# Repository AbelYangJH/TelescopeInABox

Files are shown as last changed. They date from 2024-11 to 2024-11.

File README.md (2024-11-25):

# TelescopeInABox
The Telescope In A Box is a collapsible Dobsonian Telescope

There are two models available:

- Model 2: Designed for a 114mm dia f/8 primary mirror
- Model 3: Designed for a 200mm dia f/5 primary mirror

A more detailed paper is available at https://www.worldscientific.com/doi/abs/10.1142/S2661339521500049

To cite:
> The Telescope-in-a-Box — A Collapsible Open-Frame Dobsonian Telescope for Student Astronomy Projects
> 
> A. Yang, A. H. Chan, and S. C. Cindy Ng
> 
> The Physics Educator Vol. 03, No. 01, 2150004 (2021)

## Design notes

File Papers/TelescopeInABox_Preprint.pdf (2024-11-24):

The Physics Educator
c World Scientific Publishing Company

## The Telescope-in-a-box - A collapsible open-frame Dobsonian Telescope for Student Astronomy Projects

A. Yang∗

, A. H. Chan†

, S. C. Cindy Ng.‡
Department of Physics, National University of Singapore, 2 Science Drive 3, Block S12, Level 2, Singapore 117551 ∗phyyja@nus.edu.sg
†phycahp@nus.edu.sg
‡phynsc@nus.edu.sg

Received Day Month Year
Revised Day Month Year

The telescope-in-a-box is a small objective ultralight Dobsonian telescope concept that will be accompanied by telescope instrumentation lesson plans. This provides a rich set of opportunities for teaching astronomy, physics and engineering. Our first two prototypes demonstrate that it can be constructed at low cost, while many of the design decisions can lead to lesson plans in telescope instrumentation.

Keywords: Telescopes; Practical Astronomy; Astronomical Instrumentation.

### 1. Introduction

Telescopes are an essential teaching tool in astronomy¹
, allowing students to connect in-class instruction to the real world through practical activities²
. However, many commercial telescopes are large and bulky, or have limited light collecting area. In particular, many commercially available small telescopes are of the closed tube design, while truss or ultralight designs are commercially available only for larger aperture reflectors (generally 300mm objective diameter and larger) and tend to be more expensive.
These limitations place some constraints on the use of commercially available small telescopes in a classroom setting. The closed tube design of the more affordable models limit the in-class demonstration potential in that students do not necessarily get to see the inner workings of the telescope and tend to treat it as some sort of black box. At the same time, the higher cost of the truss or ultralight models mean that mass deployment of such models are far less feasible. To solve this problem, we have developed the telescope-in-a-box, a small objective ultralight Dobsonian telescope that is inexpensive, collapsible and lightweight with an open frame. This concept is based on the guiding principles of portability, cost and educational value.
To be portable, the telescope needs to be both lightweight and collapsible. The first prototype of the telescope-in-a-box proved that a collapsible design is practical, but its carrying weight will strongly depend on the choice of materials and engineering decisions that go into the final design. In contrast with commercial ultralight Dobsonians which are designed to be lightweight first, the telescope-in-a-box is designed to be compact first, with the intention that students may borrow a telescope set for independent observations. This is especially important because in Singapore, students generally travel by public transport and that makes a large bulky tube less practical to transport. In many other parts of Southeast Asia, students often

1

2 A. Yang et. al.

travel via motorcycle which also does not allow for transporting of a large bulky tube.
To be low-cost, we need to carefully choose the objective size and structural materials. In contrast with commercial ultralight or truss Dobsonians, the telescope-in-a-box has a much smaller objective diameter. This is particularly important since the cost of a Dobsonian is primarily driven by its objective diameter.
More importantly, the telescope-in-a-box must have a rich set of educational opportunities in the classroom and in the field. That means the telescope design must be sufficiently capable on its own, while at the same time provide sufficient educational opportunities through its design. A good example of how this is accomplished is the gallileoscope³
, which
is a simple refractor that is designed to be taken apart and assembled in class, with ample opportunities to demonstrate optical principles⁴
. While the
gallileoscope was originally developed for the price point of 30 USD and does not include a tripod, the telescope-in-a-box that we have built costs about 250 USD which includes a simple Dobsonian mount.

### 2. The Tubeless Telescope-in-a-box

prototypes

In the course of its design and construction, we have constructed two prototypes for the telescope-in-abox. Prototype 1 has a 200mm f/6 primary mirror, with a focal length of 1200mm and was constructed to demonstrate the tubeless design with off-the-shelf mirror cells and focuser. In addition, the carrying case was also designed to double up as the azimuth base and rocker box. However, that meant the carrying case needed to be stronger and hence heavier. In addition, the primary mirror cell was an off-the-shelf part that was excessively heavy, but extremely sturdy. The secondary support pole used a 30mm aluminium T-slot extrusion, which is readily available and sturdy, but also very heavy. The final carrying weight of prototype 1 is 21 kg. Prototype 2 was constructed as an attempt to improve on the basic Newtonian design in addition to the tubeless design. It has a 112.5 mm f/8 primary mirror with a focal length of 900mm (taken from an existing Newtonian telescope) and was constructed to be lightweight and compact. In its collapsed form, the main parts can be packed in a small plastic box (excluding the poles and base). In particular, prototype 2 uses custom 3D printed parts (printed on a modified Flashforge Creator Pro) including the mirror cells and focuser and has a much larger altitude bearing.
In addition, prototype 2 was designed to be assembled without any special tools; It only requires a simple screwdriver for secondary collimation. To make the final design lightweight, we chose not to use the carrying case as a structural component, while the secondary support is a pair of lightweight wooden (paulownia) poles. The final carrying weight of prototype 2 is less than 3kg.

### 2.1. Design Decisions

In the course of the design and construction process, we note that the use of custom-designed parts allow for a closer examination of the physical principles underlying telescope design, and potentially allows for the teaching of iterative design methods. For example, the focuser in prototype 2 is a threaded rotating helical focuser which took multiple tries to perfect, because of manufacturing tolerance issues. To solve this, the final design used a compliant split thread that would hold the focuser tube, while at the same time be tolerant of less than ideal manufacturing precision. Similar concepts can be taught, and the choice of focuser design can also be a potential lesson plan.
In addition, the design of the mirror cells provides an opportunity to discuss the concept of kinematic couplings and degrees of freedom, while the design decisions that go into the secondary pole provide an opportunity to examine beam deflection, centre of mass and material selection. This is in contrast to the use of off-the-shelf parts such as mirror cells and focusers which lock the user in to a triedand-tested design paradigm.
The use of custom parts for prototype 2 did not result in any significant additional costs beyond 3D printing, with the final bill of materials for prototype 2 being less than USD 200. Here, the single most expensive part is the mirror set (a new mirror set with similar specifications costs USD 90; http://www.e-scopes.cc/), although it is certainly possible for amateurs to grind their own primary mirror. Amateur telescope makers have made telescopes with little more than plywood, cardboard and carpentry skills.
For prototype 2 much time was spent on multiple design iterations. While this may seem to be a disadvantage, the design iterations provide a handson experience on how the parts fit together, and the physical principles that go into the design, from

The Telescope-in-a-box 3

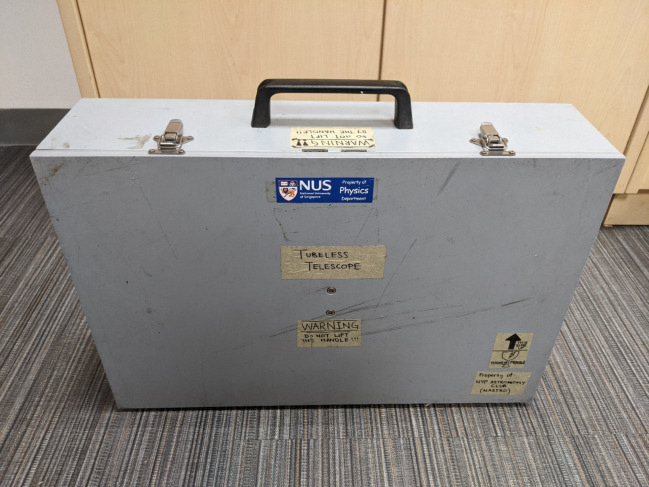
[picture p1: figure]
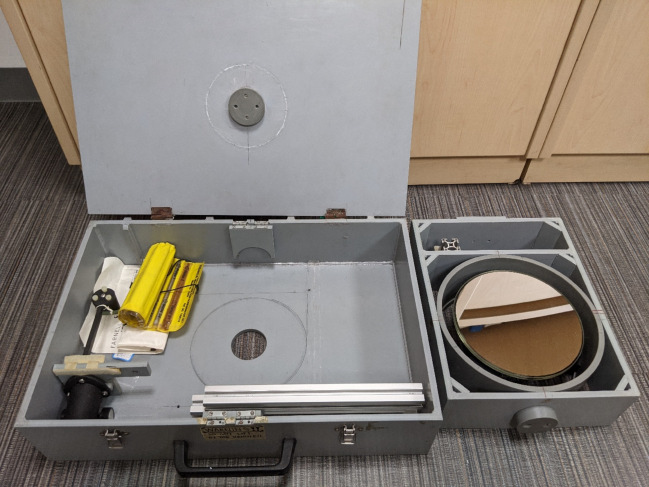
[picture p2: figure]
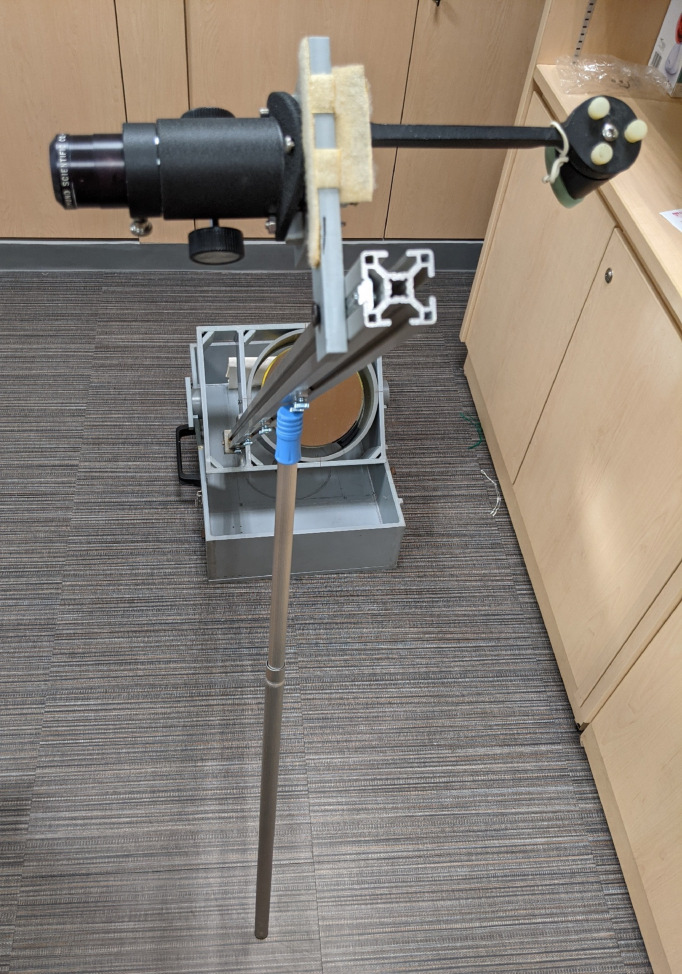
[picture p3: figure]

i.

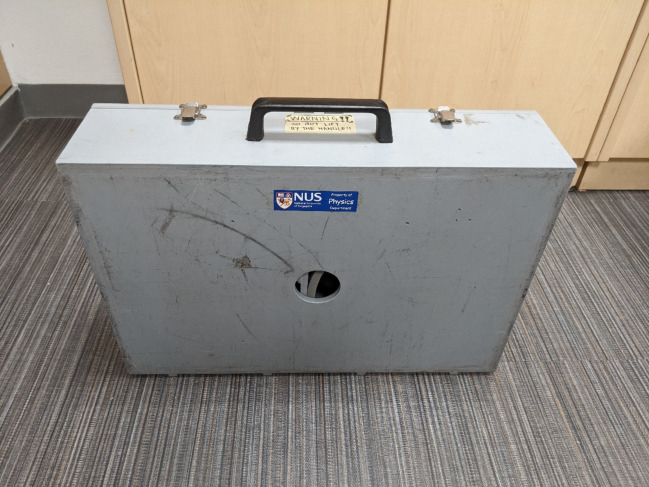
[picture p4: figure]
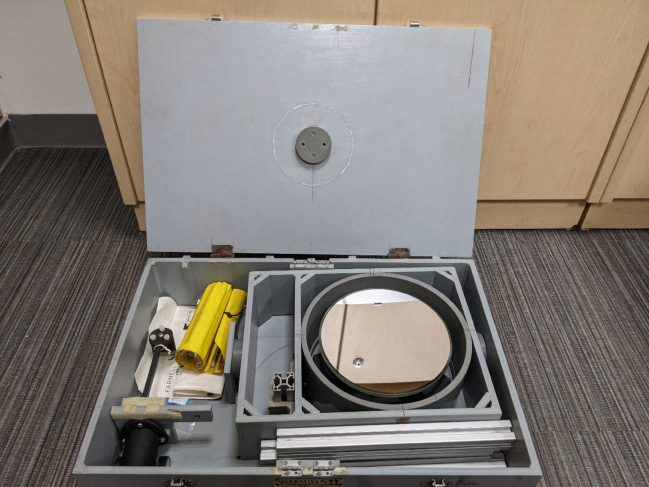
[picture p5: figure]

a. | b. | c.

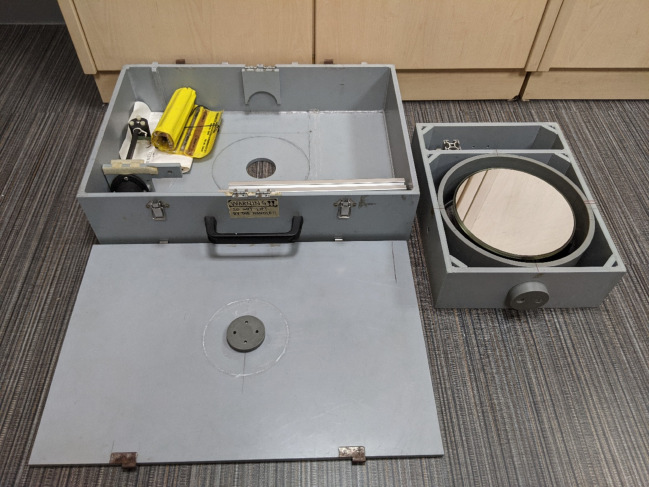
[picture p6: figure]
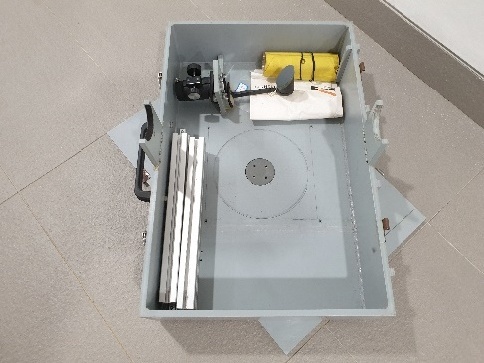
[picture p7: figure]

d. | e. | f.

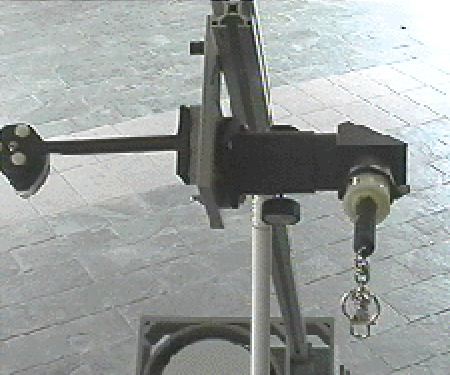
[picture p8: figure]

g.

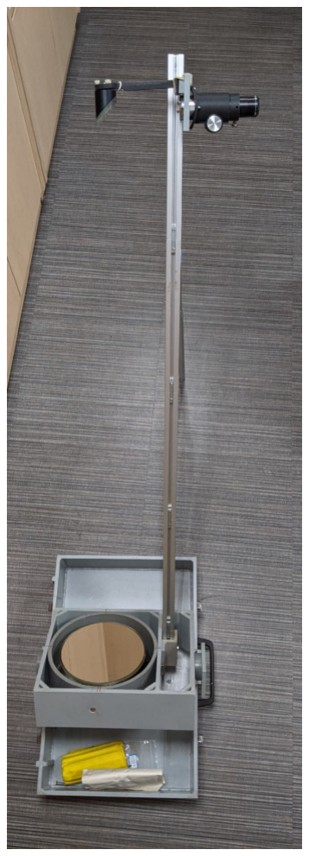
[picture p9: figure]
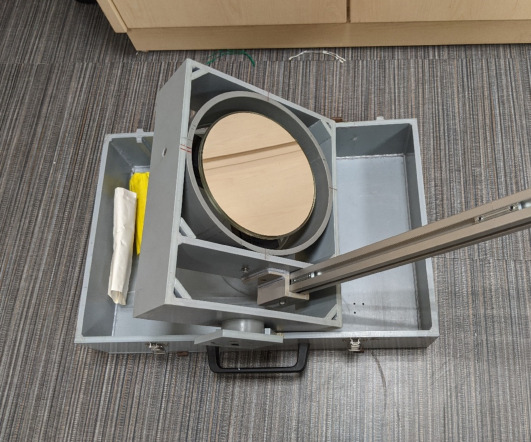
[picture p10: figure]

h. j.

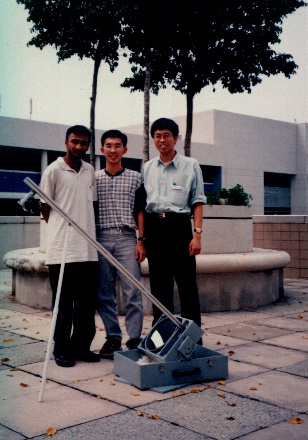
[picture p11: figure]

k.

Fig. 1. Tubeless Telescope in a box prototype 1. | a. Front view. | b. Back view (note the round hole). | c. Contents of the
box with accessories. | d. The primary mirror box taken out. | e. The separated cover (note the round peg). | f. The box is
placed on the cover and can be rotated about the peg. | g. The secondary mirror section with custom laser collimator. | h.
The primary mirror section. i. The fully assembled telescope. j. The fully assembled telescope with the secondary support pole. k. One of the authors with 2 students Arun Vythilingam and Lim Sin Hoe at Nanyang Polytechnic.

which we can construct lesson plans. Therefore instead of starting from scratch, the telescope-in-abox design and lesson plans provide a starting point for experimentation and authentic learning. More importantly, by providing a set of pre-constructed parts, the plans to make replacement spares and the design principles that go behind these parts, we set the tone that telescopes are accessible and open to

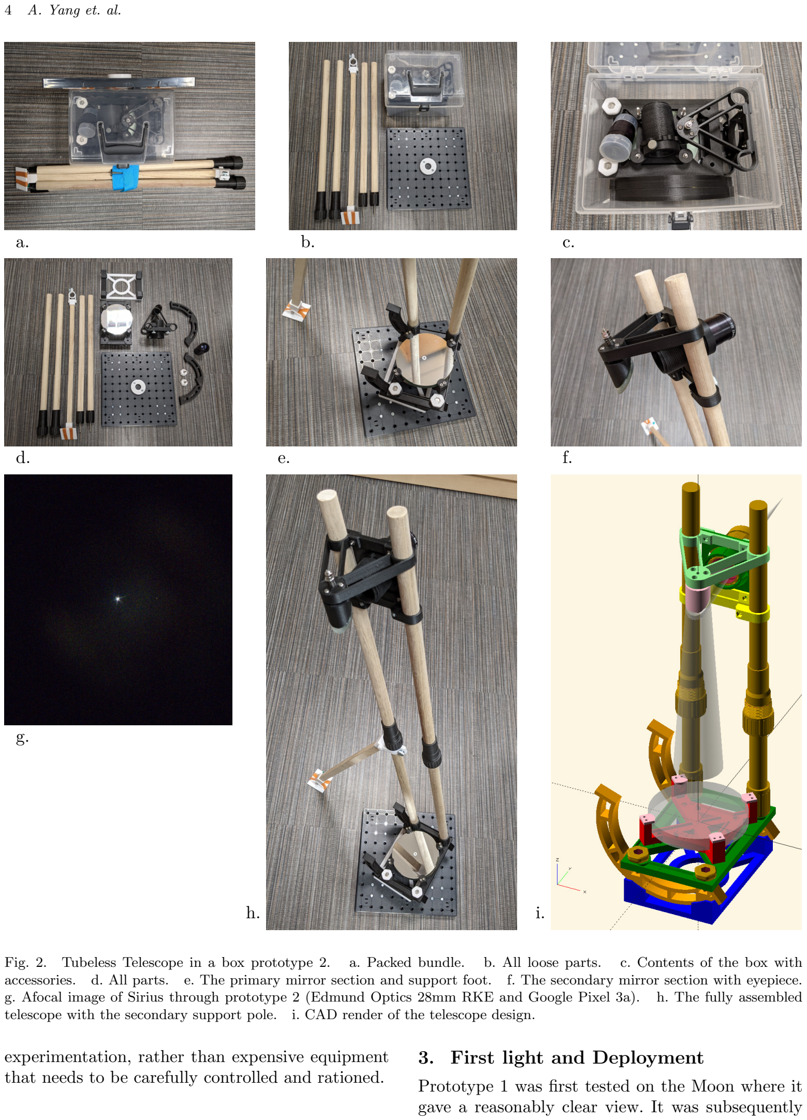
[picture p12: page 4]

4 A. Yang et. al.

a. | b. | c.
d. | e. | f.

g.

h. i.
Fig. 2. Tubeless Telescope in a box prototype 2. | a. Packed bundle. | b. All loose parts. | c. Contents of the box with
accessories. d. All parts. e. The primary mirror section and support foot. f. The secondary mirror section with eyepiece.
g. Afocal image of Sirius through prototype 2 (Edmund Optics 28mm RKE and Google Pixel 3a). h. The fully assembled telescope with the secondary support pole. i. CAD render of the telescope design.

experimentation, rather than expensive equipment
that needs to be carefully controlled and rationed.

### 3. First light and Deployment

Prototype 1 was first tested on the Moon where it gave a reasonably clear view. It was subsequently

The Telescope-in-a-box 5

deployed on a number of observing field trips. Prototype 2 was tested on Sirius with a 28mm Edmund Optics RKE eyepiece, and performed reasonably well for a very lightweight telescope. Vibrations damped out reasonably fast in about 5 seconds. Diffraction spikes were somewhat strong and 6-pointed because of the secondary support design. The only problem with the design was balance, where the secondary side was too heavy. This meant that the lowest practical altitude was about 40 degrees without additional support. Adding a counterweight and replacing the 3d-printed lower section with one machined from aluminium or steel would help this problem by lowering the centre-of-mass.

### 4. Future Work

The telescope-in-a-box concept is not complete in its current form. Many of the design decisions that go into building these prototypes can be written into lesson plans that demonstrate one or more physics or engineering concepts in telescope instrumentation. In addition, these concepts can also be used to redesign the basic structure to accommodate telescope mirrors of different sizes and we plan for subsequent models to have 200mm f/5 and 150mm f/5 mirrors, and to utilise not just 3D printing but also allow for parts to be made in a traditional machine shop. This will allow for parts made of stronger materials such as aluminium, steel or wood. We plan to make the design open source, with multiple design options depending on available fabrication capabilities.
Finally, as a stretch goal, we see the possibility of adding automatic tracking capabilities through the addition of two stepper motors and a microcontroller, which will open up further lesson plans and turn the telescope-in-a-box into a fully-featured telescope system.

Appendix
Specifications of prototype 1 (as built)

Box Dimensions
390 mm × 585 mm × 150 mm
Central Hub Diameter
60 mm
Fully Extended Height
1560 mm
Box Material
Rigid PVC

Total Carrying Weight
21 kg
Estimated Cost
USD 750

Specifications of prototype 2 (as built)

Box Dimensions
223 mm × 175 mm × 150 mm
(excluding poles/base)
Central Hub Diameter
50 mm
Fully Extended Height
1000 mm
Telescope Structural Material Carbon-fibre impregnated PETG Total Carrying Weight
3 kg
Estimated Cost
USD 200

Prototype 2 Bill of Materials (as built)

- 1× Mirror set: USD 90.00 (http://www.e-scopes.cc/)
- 1 kg PETG-CF filament: USD 35.00 (Aliexpress)
- 4× 20mm dia×450mm wood pole: USD 6.00
- 1× 15mm sq.×450mm wood pole: USD 1.50
- 1× Base Plate: USD 1.50
- 1× Carrying Case: USD 1.50
- Fasteners and springs: USD 20.00 (est.)
- 4× M6×30mm hex head screw
- 4× M6 nut
- 6× M4×40mm hex head screw
- 2× M4×10mm thumbscrew
- 8× M4 nut
- 1× M4 washer
- 3× 5mm ID×20mm spring
- 3× M3×20mm philips head screw
- 4× M3×15mm philips head screw
- 2× M3×10mm thumbscrew
- 9× M3 nut
- 6× 3.5mm × 12mm woodscrew

References

1. I. C. Jacobi, H. J. Newberg, R. A. F. Darren Broder,
A. J. Milano, A. T. W. Lee A. Newberg and D. C. B. Whittet, Astronomy Education Review 7, 66 (2008).

6 A. Yang et. al.

2. A. Yang, S. C. C. Ng, Q. Leong, M. H. Tan, P. Agarwal, Z. Ong, H. W. Ang and A. H. Chan, The Physics Educator 01, p. 1950004 (2019).
3. S. M. Pompea, R. N. Pfisterer, S. Ellis, D. N. Arion,
R. T. Fienberg and T. C. Smith, Optical and system engineering in the development of a high-quality student telescope kit, in Modeling, Systems Engineering, and Project Management for Astronomy IV , eds.
G. Z. Angeli and P. Dierickx (SPIE, 2010).
4. S. M. Pompea, R. T. Sparks, C. E. Walker and
E. F. C. Dokter, Optics education through the Arizona Galileoscope program, in Optics Education and Outreach II, ed. G. G. Gregory (SPIE, 2012).

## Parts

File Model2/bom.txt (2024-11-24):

Bill of Materials

Model 2 - 1148v4

M6 Nut x4
M6x20 hex head bolt x4

M4x40 hex head bolt x5
M4 spring x3
M4 nut x8
M4x15 thumb screw x2

M3x10 screw x8
M3x20 screw x2
M3 nut x7
M3x15 screw x4
M3x10 thumbscrew x1

20mmx450mm dia pole x4
15mmx450mm square pole x1

Count	Material	Filament (g)	File
1	PETG-CF	96	1148FDM-BASE-AziBlock-1.0-PCE.stl
1	PETG	20	1148FDM-BASE-BaseHub-1.0-PPE.stl
1	PETG-CF	47	1148FDM-BASE-RockerL-1.0-PCE.stl
1	PETG-CF	47	1148FDM-BASE-RockerR-1.0-PCE.stl
1	PETG-CF	5	1148FDM-FOCA-ActiveLock-F317-1.0-PCE.stl
	PETG-CF		1148FDM-FOCA-EndLock-F317-1.0-PCE.stl
1	PETG-CF	38	1148FDM-FOCA-FocusTube-F317-1.0-PCE.stl
2	PETG-CF	5	1148FDM-PRIC_BaseKnob-1.0-PCE.stl
2	PETG-CF	3	1148FDM-PRIC_CollBolt-1.0-PCE.stl
2	PETG-CF	2	1148FDM-PRIC-CollKnob-1.0-PCE.stl
	PETG		1148FDM-PRIC-Counterweight-1.0-PPE.stl
1	PETG-CF	86	1148FDM-PRIC-LowerCell-1.0-PCE.stl
1	PETG-CF	54	1148FDM-PRIC-MirrorCell-1.0-PCE.stl
4	PETG-CF	1	1148FDM-PRIC-TopClip-1.0-PCE.stl
2	PETG	4	1148FDM-SARM-ColletClamp-1.0-PPE.stl
2	PETG-CF	21	1148FDM-SARM-ColletJoint-1.0-PCE.stl
2	PETG-CF	9	1148FDM-SARM-ColletLock-1.0-PCE.stl
1	PETG	9	1148FDM-SARM-FinderMount-1.0-PPE.stl
1	PETG	18	1148FDM-SARM-FootBase-1.0-PPE.stl
1	PETG	14	1148FDM-SARM-FootClamp-1.0-PPE.stl
	PETG-CF		1148FDM-SARM-MiddleClamp-1.0-PCE.stl
2	PETG-CF	14	1148FDM-SARM-PoleBase-1.0-PCE.stl
1	PETG-CF	21	1148FDM-SECA-BackPlate-F317-1.0-PCE.stl
1	PETG-CF	25	1148FDM-SECA-LowerClamp-1.0-PCE.stl
1	PETG-CF	10	1148FDM-SECA-MirrorPad-1.0-PCE.stl
1	PETG-CF	29	1148FDM-SECA-Spider-1.0-PCE.stl
1	PETG-CF	4	1148FDM-SECA-TiltPlate-1.0-PCE.stl

PETG-CF	574g
PETG	69g

System Spec
1148FDM	114mm f/8 FDM Primary cell

Subassembly
PRIC	Primary Cell
BASE	Rocker Base
SARM	Secondary Arm
SECA	Secondary Assembly
FOCA	Focuser

PartID
PRIC-BaseKnob
PRIC-CollBolt
PRIC-CollKnob
PRIC-Counterweight	Beta
PRIC-LowerCell
PRIC-MirrorCell
PRIC-TopClip
SARM-ColletClamp
SARM-ColletJoint
SARM-ColletLock
SARM-FinderMount
SARM-FootBase
SARM-FootClamp
SARM-MiddleClamp	Beta
SARM-PoleBase
BASE-RockerL
BASE-RockerR
BASE-AziBlock
BASE-Azihub	TODO
SECA-BackPlate
SECA-LowerClamp
SECA-MirrorPad
SECA-Spider
SECA-TiltPlate
FOCA-ActiveLock
FOCA-EndLock	Beta
FOCA-FocusTube

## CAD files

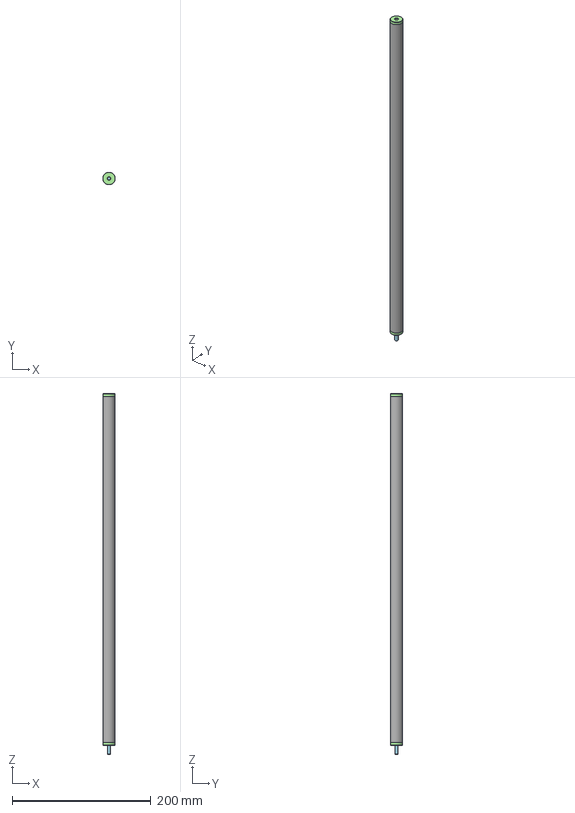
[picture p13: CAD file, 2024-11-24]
Model3v2/CAD/PoleAssembly.FCStd
18.0 x 18.0 x 521.0 mm
PoleBase x 2
Pole_Body
M5x16-Screw
M5-Nut

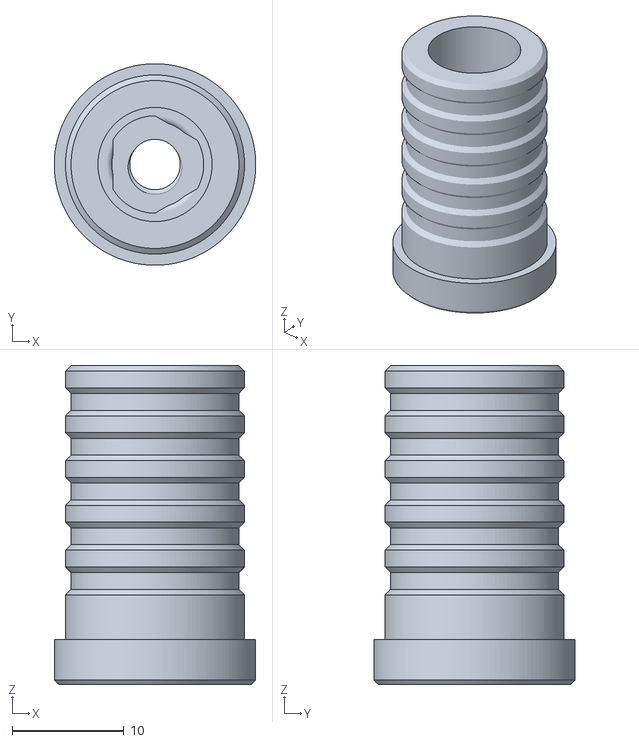
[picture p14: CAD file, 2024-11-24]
Model3v2/STL/PoleAssembly-PoleBaseThreaded_4x.stl
18.0 x 18.0 x 28.5

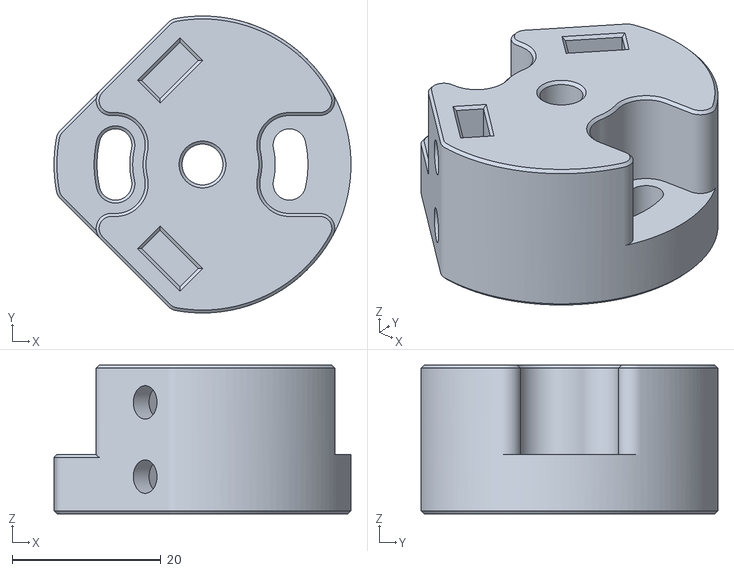
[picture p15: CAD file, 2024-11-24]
Model3v2/STL/SecondaryMirrorCell-SpiderHub_Main_1x.stl
40.0 x 40.0 x 20.0

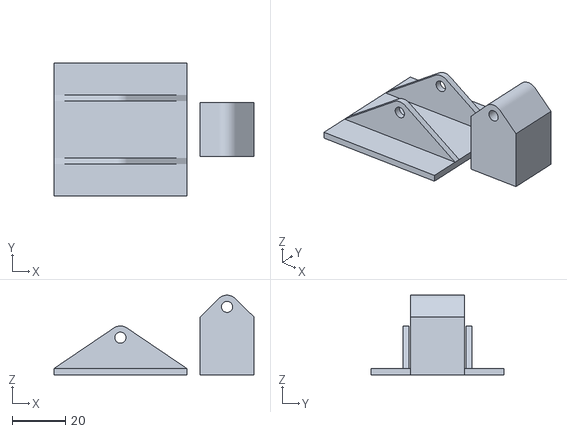
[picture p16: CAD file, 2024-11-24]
Model2/1148FDM-SARM-FootBase.stl
75.3 x 50.0 x 30.0

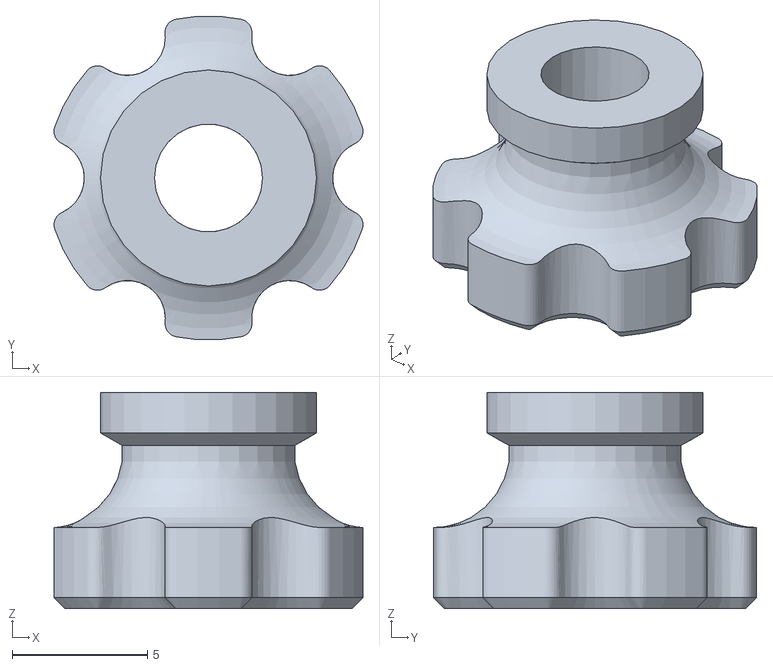
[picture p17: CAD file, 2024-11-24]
Model3v2/Extras/Knobs-M4HexCover.stl
11.4 x 12.0 x 8.00

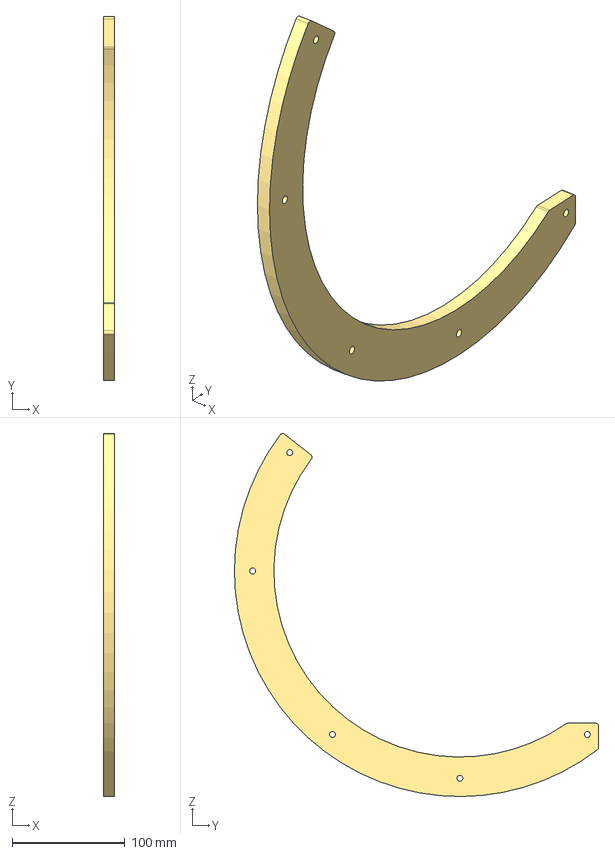
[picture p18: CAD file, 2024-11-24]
Model3v2/STEP/Primary-RockerRail.step
10.0 x 323.0 x 322.0 mm

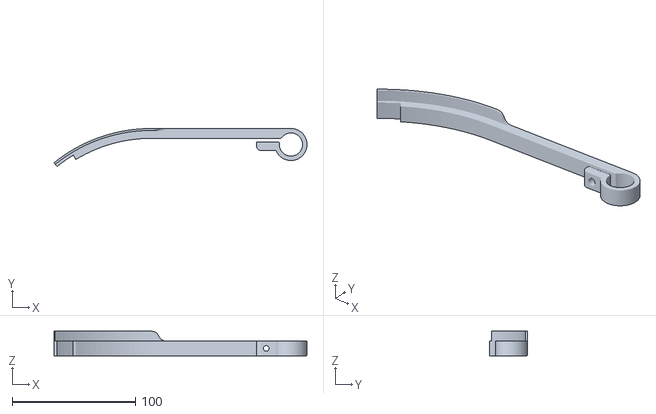
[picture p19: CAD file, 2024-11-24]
Model3v2/STL/Secondary-UpperArcA_1x.stl
204.9 x 30.8 x 20.0

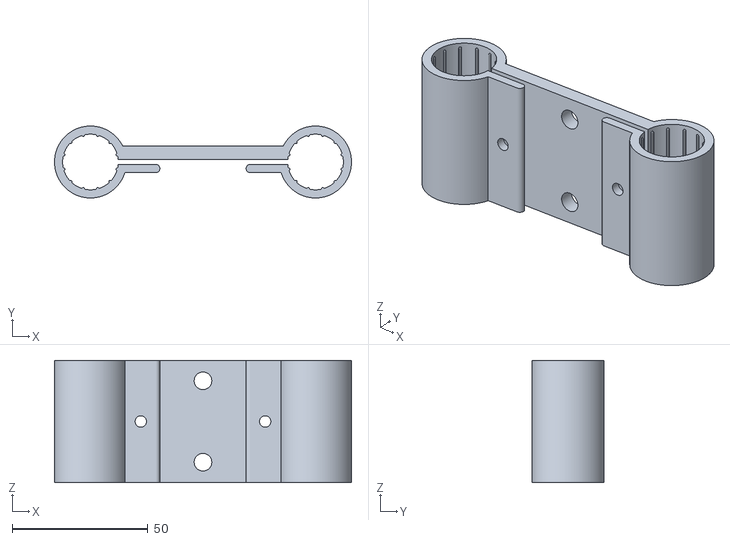
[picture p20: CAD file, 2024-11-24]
Model2/1148FDM-SARM-MiddleClamp.stl
109.4 x 26.5 x 45.0

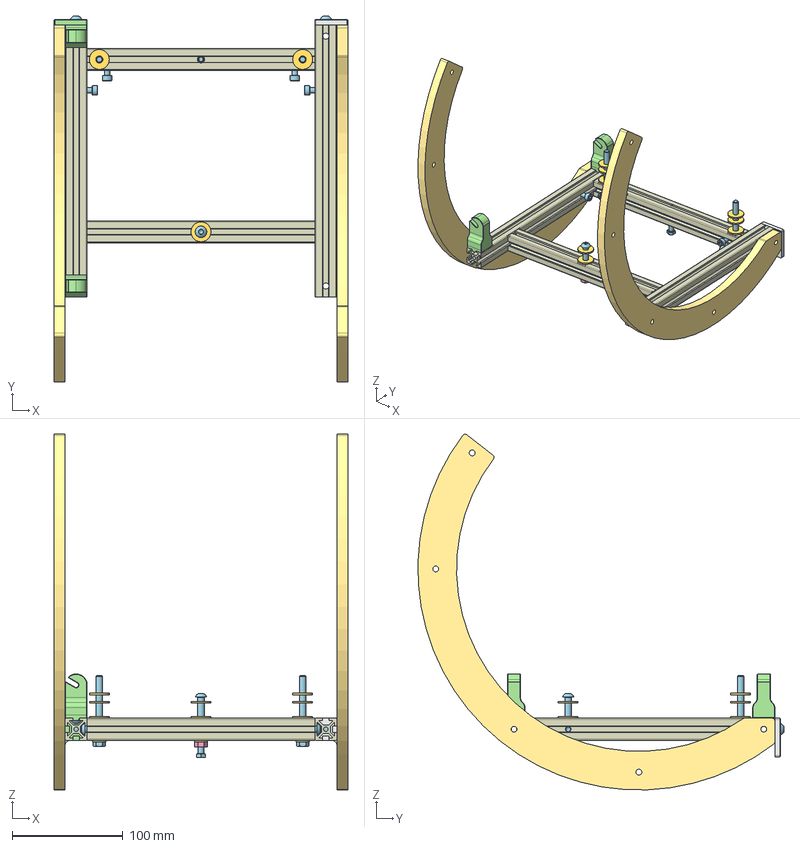
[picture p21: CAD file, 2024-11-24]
Model3v2/CAD/Primary.FCStd
266.0 x 331.2 x 321.8 mm
Frame_A
Frame_PS x 2
Frame_F
SideArmBase x 2
M5x16-Screw
M5x16-Screw001
EndStopper
EndStopper_M
M6x60-Screw
M6x60-Screw001
M6-Washer
M6-Washer313
M6-Washer314
M6-Washer315
M6-Washer316
M6-Washer317
M6-Washer318
M6-Washer319
M6-Washer320
M6-Washer321
M6x45-Screw
M6-Nut
M6-Washer322
M6x16-Screw
M6x16-Screw001
M6x10-Screw
M6x10-Screw001
M5x8-Screw
M5x8-Screw086
M5x8-Screw087
M5x8-Screw088
RockerRail x 2
M5x20-Screw

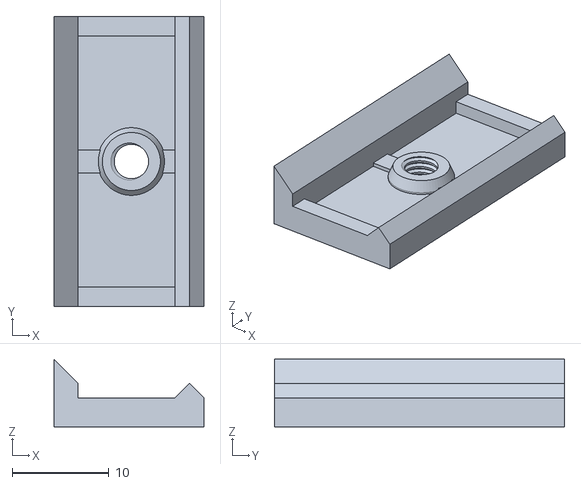
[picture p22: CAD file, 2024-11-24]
Model3v2/Extras/FinderClamp-ClampThreaded.stl
15.5 x 30.0 x 7.00

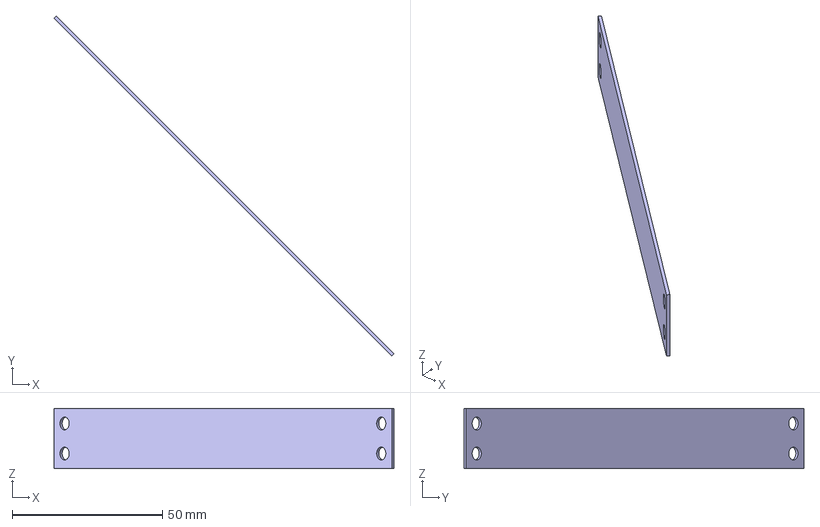
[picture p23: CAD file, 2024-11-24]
Model3v2/STEP/Secondary-SpiderVane.step
113.2 x 113.2 x 20.0 mm

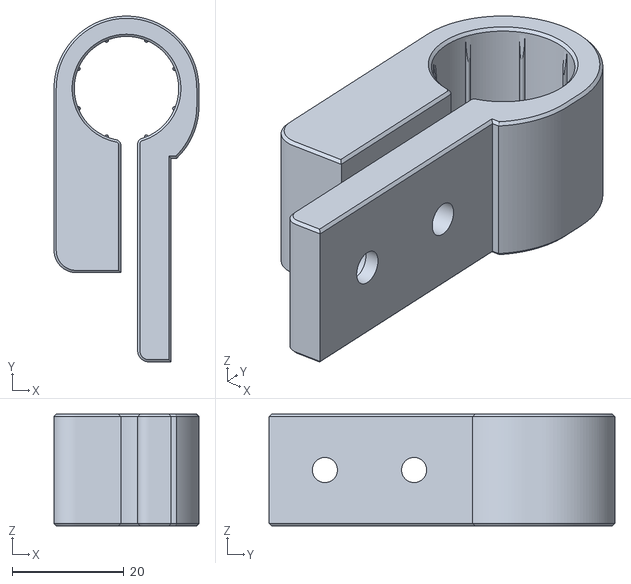
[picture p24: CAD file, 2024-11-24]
Model3v2/STL/Secondary-LowerClamp_2x.stl
26.0 x 62.0 x 20.0

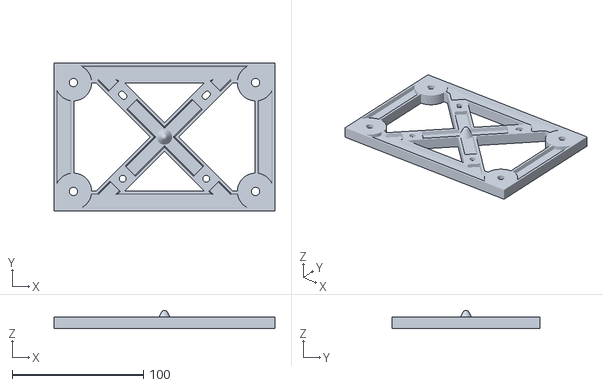
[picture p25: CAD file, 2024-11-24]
Model2/1148FDM-PRIC-LowerCell.stl
168.5 x 112.5 x 14.0

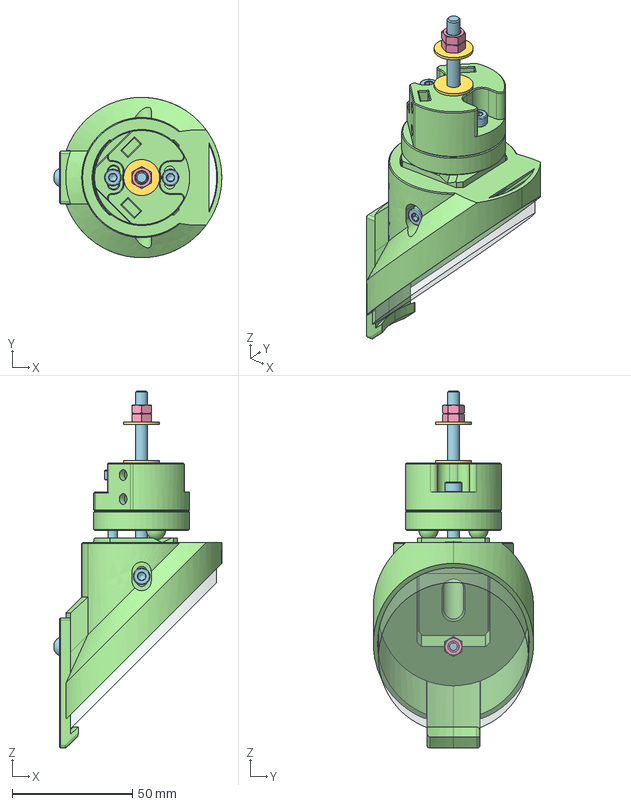
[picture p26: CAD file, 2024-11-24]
Model3v2/CAD/SecondaryMirrorCell.FCStd
69.8 x 66.8 x 148.7 mm
SecondaryMirror
MirrorCap
MirrorPad
TiltPlate
SpiderHub_Main
SecondaryClip
M4-Nut
M4x8-Screw
M5x65-Screw
M5-Washer
M5-Washer001
M5-Nut
M5-Nut001
M4x16-Screw
M4x25-Screw
M4x12-Screw
M4x12-Screw001

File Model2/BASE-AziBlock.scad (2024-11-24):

include <FullAssembly.scad>
/* [Hidden] */
isStandalone=false;
$fa=1;

// Rocker-Base
rotate(90) AzimuthBlock(rail_dia, rail_width, rail_thick, pole_x, pole_y, pri_poledia, fthick, get_fwidth(clipbolt, collbolt));

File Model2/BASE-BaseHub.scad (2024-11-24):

include <FullAssembly.scad>
/* [Hidden] */
isStandalone=false;
$fa=1;

// Rocker-Base
cylinder(d=50,h=15);

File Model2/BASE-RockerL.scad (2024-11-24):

include <FullAssembly.scad>
/* [Hidden] */
isStandalone=false;
$fa=1;

rotate([90,0,0])
// Rocker-L
rocker(altmin, rail_dia, rail_tab, rail_width, rail_thick, basebolt, pole_x, boxsize, rail_height, lowercell_z-fthick);

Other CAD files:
Model3v2/CAD/Complete.FCStd
Model3v2/STL/PoleAssembly-PoleBase_4x.stl
Model3v2/STEP/Focuser-FocuserPlate.step
Model3v2/STL/Focuser-FocuserBase_1x.stl
Model2/BASE-RockerR.scad
Model2/1148FDM-BASE-AziBlock.stl
Model2/1148FDM-BASE-BaseHub.stl
Model2/1148FDM-BASE-RockerL.stl
Model2/1148FDM-BASE-RockerR.stl
Model2/1148FDM-FOCA-ActiveLock.stl
Model2/1148FDM-PRIC-CollKnob.stl
Model2/1148FDM-PRIC-TopClip.stl
Model2/1148FDM-PRIC_BaseKnob.stl
Model2/1148FDM-PRIC_CollBolt.stl
Model2/1148FDM-SARM-ColletClamp.stl
Model2/1148FDM-SARM-FinderMount.stl
Model2/1148FDM-SARM-FootClamp.stl
Model2/1148FDM-SARM-PoleBase.stl
Model2/1148FDM-SECA-BackPlate.stl
Model2/1148FDM-SECA-LowerClamp.stl
Model2/1148FDM-SECA-MirrorPad.stl
Model2/1148FDM-SECA-Spider.stl
Model2/1148FDM-SECA-TiltPlate.stl
Model2/Collet.scad
Model2/FOCA-ActiveLock.scad
Model2/FOCA-EndLock.scad
Model2/FOCA-FocusTube.scad
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

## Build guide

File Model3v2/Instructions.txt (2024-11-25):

Machined parts:

PrimaryMirrorCell-UpperCell.step	: 1x Al6061
Primary-RockerRail.step	: 2x Al6061

Cut parts:

Focuser-FocuserPlate.step	: 1x SS304
Secondary-SpiderVane.step	: 1x SS304

Printed parts (FDM):

All parts unless specified:
0.2mm layer height, 30-40% gyroid or grid infill, 3 perimeters of 0.6mm or 4 perimeters of 0.4mm, top and bottom layers 1mm min thickness
0.4mm or 0.6mm nozzle
ABS or PETG

Base-BaseBearingTop_1x.stl	: ABS or PETG
Base-BasePadSide_4x.stl	: ABS or PETG
Base-BaseWheel_4x.stl	: TPU/TPE 25-30% infill, 2 walls, infill width 0.4mm, No top and bottom layers, random scarf seam
Base-BaseWheelBlockSB_4x.stl	: ABS or PETG
Base-SideGuardPostA_2x.stl	: PETG
Base-SideGuardPostB_2x.stl	: PETG
BracePole-Pivot_4x.stl	: ABS or PETG
BracePole-PoleClamp_2x.stl	: ABS or PETG
Common-CounterWeightClamp_1x.stl	: ABS or PETG
Focuser-EyepieceAdaptor_1x.stl	: Black ABS or PETG
Focuser-FocuserBase_1x.stl	: Black ABS or PETG
Focuser-FocuserSpring_1x.stl	: Black ABS or PETG
Focuser-FocuserTube_1x.stl	: Black ABS or PETG
PoleAssembly-PoleBase_4x.stl	: ABS or PETG
PoleAssembly-PoleBaseThreaded_4x.stl	: ABS or PETG
Primary-EndStopperA_1x.stl	: ABS or PETG
Primary-EndStopperB_1x.stl	: ABS or PETG
PrimaryMirrorCell-LowerPad_3x.stl	: ABS or PETG
PrimaryMirrorCell-MirrorClip_4x.stl	: Black ABS or PETG
PrimaryMirrorCell-PrimaryMirrorCover_x1.stl	: ABS or PETG
Primary-SideArmBase_2x.stl	: Black ABS or PETG
Secondary-LowerClamp_2x.stl	: Black ABS or PETG
SecondaryMirrorCell-MirrorCap_1x.stl	: Black ABS or PETG
SecondaryMirrorCell-MirrorPad_1x.stl	: Black ABS or PETG
SecondaryMirrorCell-SecondaryClip_1x.stl	: Black ABS or PETG
SecondaryMirrorCell-SpiderHub_Main_1x.stl	: Black ABS or PETG
SecondaryMirrorCell-TiltPlate_1x.stl	: Black ABS or PETG
Secondary-MirrorCover_625_x1.stl	: ABS or PETG
Secondary-MirrorCoverCap_625_x1.stl	: ABS or PETG
Secondary-UpperArc_1x.stl	: ABS or PETG
Secondary-UpperArcA_1x.stl	: ABS or PETG
Secondary-UpperArcB_1x.stl	: ABS or PETG
Secondary-UpperArcC_1x.stl	: ABS or PETG
Secondary-UpperClamp_2x.stl	: Black ABS or PETG

Printed parts (SLS):

The following parts may alternatively be printed in SLS PA12:
Common-CounterWeightClamp_1x.stl
Primary-EndStopperA_1x.stl
Primary-EndStopperB_1x.stl
PrimaryMirrorCell-MirrorClip_4x.stl	: Black
Secondary-LowerClamp_2x.stl	: Black
SecondaryMirrorCell-MirrorPad_1x.stl	: Black
SecondaryMirrorCell-SpiderHub_Main_1x.stl	: Black
SecondaryMirrorCell-TiltPlate_1x.stl	: Black
Secondary-UpperClamp_2x.stl	: Black

Additional Post-processing:
The following parts have a slot to thread a nylon zip-tie that will serve as a wear-pad for the altitude and azimuth bearing. This is intended to reduce stiction between the rail and the block.
Base-SideGuardPostA_2x.stl
Base-SideGuardPostB_2x.stl

Bill of Materials:

Item	Diameter	Length	Type	Qty.
M2x10-Screw(self tapping)	M2	10	self tapping	4
M3-Nut(DIN985)	M3		DIN985	3
M3-Washer(ISO7092)	M3		ISO7092	9
M3x25-Screw(ISO7380-1)	M3	25	ISO7380-1	3
M4x12-Screw(GBT834)	M4	12	GBT834	2
M4x20-Screw(GBT834)	M4	20	GBT834	6
M4x25-Screw(GBT834)	M4	25	GBT834	9
M4x16-Screw(ISO10642)	M4	16	ISO10642	4
M4-Nut(ISO4032)	M4		ISO4032	9
M4x8-Screw(ISO4762)	M4	8	ISO4762	4
M4x12-Screw(ISO4762)	M4	12	ISO4762	2
M4x12-Screw(ISO4762)	M4	12	ISO4762	4
M4x16-Screw(ISO4762)	M4	16	ISO4762	1
M4x20-Screw(ISO4762)	M4	20	ISO4762	6
M4x25-Screw(ISO4762)	M4	25	ISO4762	1
M4x40-Screw(ISO4762)	M4	40	ISO4762	8
M4-Washer(ISO7089)	M4		ISO7089	8
M4x8-Screw(ISO7380-1)	M4	8	ISO7380-1	11
M4x12-Screw(ISO7380-1)	M4	12	ISO7380-1	3
M5x16-Screw(GBT834)	M5	16	GBT834	4
M5x16-Screw(ISO4017)	M5	16	ISO4017	4
M5x20-Screw(ISO4017)	M5	20	ISO4017	1
M5x65-Screw(ISO4017)	M5	65	ISO4017	1
M5-Nut(ISO4032)	M5		ISO4032	6
M5x8-Screw(ISO4762)	M5	8	ISO4762	12
M5x10-Screw(ISO4762)	M5	10	ISO4762	4
M5-Washer(ISO7093-1)	M5		ISO7093-1	2
M5x16-Screw(ISO7380-1)	M5	16	ISO7380-1	2
M6-Nut(DIN466)	M6		DIN466	2
M6x60-Screw(ISO4017)	M6	60	ISO4017	2
M6-Nut(ISO4032)	M6		ISO4032	1
M6-Washer(ISO7089)	M6		ISO7089	3
M6-Washer(ISO7093-1)	M6		ISO7093-1	8
M6x10-Screw(ISO7380-1)	M6	10	ISO7380-1	2
M6x16-Screw(ISO7380-1)	M6	16	ISO7380-1	8
M6x45-Screw(ISO7380-1)	M6	45	ISO7380-1	1
Misumi HBLFSN5 equiv.				6
Misumi HNTT5-5 equiv				23
Misumi HNTT5-4 equiv				4
9.2mm ID 12mm OD 25mm L SS304 Spring				4
M4x6x4 insert				29
S623 bearing				6
S624 bearing				4
large nylon zip-ties	8
